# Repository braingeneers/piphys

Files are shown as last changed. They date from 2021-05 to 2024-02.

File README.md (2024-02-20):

# piphys

Update: The latest manuscript about Piphys has been published in IOP Journal of Neural Engineering!

Peer-reviewed journal article: 

[Light-weight electrophysiology hardware and software platform for cloud-based neural recording experiments](https://iopscience.iop.org/article/10.1088/1741-2552/ac310a/pdf)

The original [preprint](https://www.biorxiv.org/content/10.1101/2021.05.18.444685v2) can still be accessed on bioRxiv.

--------
## Overview

Piphys is an inexpensive open source neurophysiological recording platform based on Raspberry Pi. It is easily accessed and controlled via a standard web interface through Internet of Things (IoT) protocols. 

Piphys modules can be used in a fleet to enable long-term observations of neural development, organization, and activity at scale. 

## Design Files

### Hardware
- Raspberry Pi expansion circuit board for and Intan RHD2000 bioamplifier chip.
- Electrode adapter circuit board for Axion CytoView MEA Plate.

Source files, documentation, and files for manufacturing each circuit board are in [`./Hardware`](https://github.com/braingeneers/piphys/tree/main/Hardware).

#### Electrode mapping

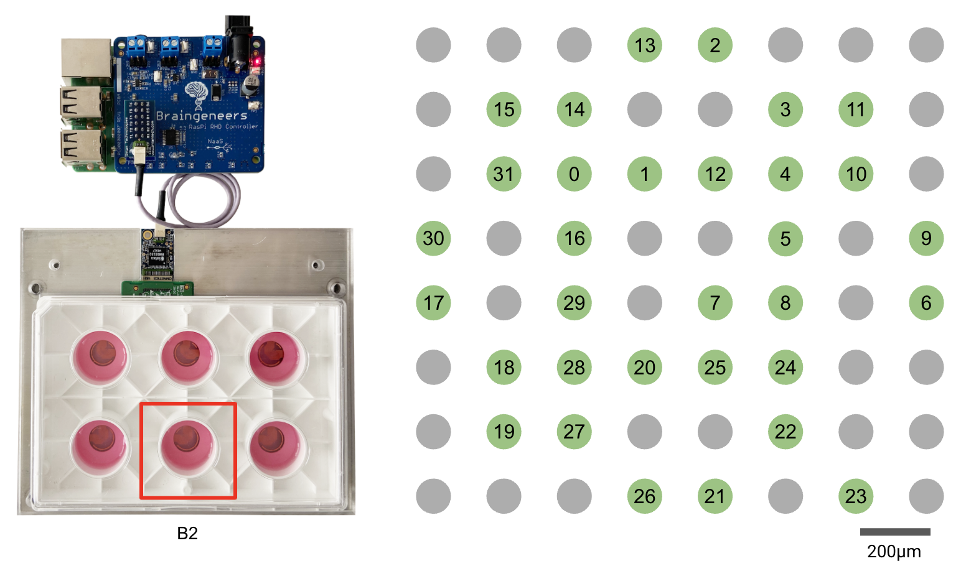
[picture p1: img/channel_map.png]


There are 64 electrodes in a well B2 of the Axion CytoView MEA Plate. The electrode adapter circuit board allows 32 of the 64 electrodes to be recorded by Piphys. The green dots are the recorded channels, labeled with their channel number in the data file sampling sequence.

### Mechanical
CAD files in for the electrode plate holder are in [`./Mechanical/AxionPlateHolder`](https://github.com/braingeneers/piphys/tree/main/Mechanical/AxionPlateHolder).

Assembly Order:
```
AxionPlateHolder_CNC_ClampTop_Aluminum
---------------------------------------
[Axion CytoView MEA Plate]
---------------------------------------
AxionPlateHolder_CNC_ClampBottom_Plastic
AxionPlateHolder_CNC_ClampBottom_Aluminum
```

### Software
Software to enable voltage sampling and user interaction, with accompanying documentation are in [`./Software`](https://github.com/braingeneers/piphys/tree/main/Software).

See [`braingeneerpy`](https://github.com/braingeneers/braingeneerspy) Python package for IoT communication library.

### Test Data
System validation data with sine wave are available at the Piphys [`Google Drive folder`](https://drive.google.com/drive/folders/1S5Uj3old0Q09hUaioH9NGgg6K85ICtAz?usp=sharing).

----
### UC Santa Cruz (UCSC) Noncommercial License

Acceptance

In order to get any license under these terms, you must agree to them as both strict obligations and conditions to all your licenses.

Copyright License

The licensor grants you a copyright license for the repository to do everything you might do with the repository that would otherwise infringe the licensor's copyright in it for any permitted purpose.

Notices

You must ensure that anyone who gets a copy of any part of the repository from you also gets a copy of these terms, as well as the following copyright notice:

This repository is Copyright © 2021. The Regents of the University of California (“Regents”). All Rights Reserved.

Noncommercial Purposes

Any noncommercial purpose is a permitted purpose.

Commercial Purposes

Contact Innovation Transfer, UC Santa Cruz, techno@ucsc.edu , https://officeofresearch.ucsc.edu/iatc/ , for any commercial purpose.

Personal Uses

Personal use for research, experiment, and testing for the benefit of public knowledge, personal study, private entertainment, hobby projects, amateur pursuits, or religious observance, without any anticipated commercial application, is use for a permitted purpose.

Noncommercial Organizations

Use by any charitable organization, educational institution, public research organization, public safety or health organization, environmental protection organization, or government institution is use for a permitted purpose regardless of the source of funding or obligations resulting from the funding.

Fair Use

You may have "fair use" rights for the repository under the law. These terms do not limit them.

No Other Rights

These terms do not allow you to sublicense or transfer any of your licenses to anyone else, or prevent the licensor from granting licenses to anyone else.  These terms do not imply any other licenses.

Patent Defense

If you make any written claim that the repository infringes or contributes to infringement of any patent, all your licenses for the repository granted under these terms end immediately. If your company makes such a claim, all your licenses end immediately for work on behalf of your company.

Violations

The first time you are notified in writing that you have violated any of these terms, or done anything with the repository not covered by your licenses, your licenses can nonetheless continue if you come into full compliance with these terms, and take practical steps to correct past violations, within 32 days of receiving notice.  Otherwise, all your licenses end immediately.

No Liability

As far as the law allows, the repository comes as is, without any warranty or condition, and the licensor will not be liable to you for any damages arising out of these terms or the use or nature of the repository, under any kind of legal claim.

Definitions

The "licensor" is Regents, and the "repository" is the repository the licensor makes available under these terms.

"You" refers to the individual or entity agreeing to these terms.

"Your company" is any legal entity, sole proprietorship, or other kind of organization that you work for, plus all organizations that have control over, are under the control of, or are under common control with that organization.  

"Control" means ownership of substantially all the assets of an entity, or the power to direct its management and policies by vote, contract, or otherwise.  Control can be direct or indirect.

"Your licenses" are all the licenses granted to you for the repository under these terms.

"Use" means anything you do with the repository requiring one of your licenses.

© 2021 Braingeneers

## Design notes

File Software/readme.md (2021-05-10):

# Raspberry Pi - intan RHD Software with IoT interface

## Enviornment Setup:
  Libraries and dependencies are installed to default path /usr/local
- ### bcm2835 
  C library for Broadcom BCM 2835 to access SPI. *[Link](https://www.airspayce.com/mikem/bcm2835/)*    
  
  __Install:__
  ```
  # download the latest version of the library, say bcm2835-1.xx.tar.gz, then:
  tar zxvf bcm2835-1.xx.tar.gz 
  cd bcm2835-1.xx
  ./configure
  make
  sudo make check
  sudo make install     
  ```

- ### redis-plus-plus
  C++ client library for Redis. *[Link](https://github.com/sewenew/redis-plus-plus)*  
  
  __Install:__
  ```
  # first install hiredis
  git clone https://github.com/redis/hiredis.git
  cd hiredis
  make
  make install
  
  # then install redis-plus-plus with cmake
  git clone https://github.com/sewenew/redis-plus-plus.git
  cd redis-plus-plus
  mkdir compile
  cd compile
  cmake -DCMAKE_BUILD_TYPE=Release ..
  make
  make install
  cd ..
  ```
  
- ### JsonCpp
  C++ library to manipulate Json files. *[Link](https://github.com/open-source-parsers/jsoncpp)*
  
  __Install:__
  ```
  sudo apt-get install libjsoncpp-dev
  ```
  - __Note:__ Using the vcpkg dependency manager as said in the instruction on JsonCpp's github page may stuck the pi. The header file using *apt-get install* should be included as <jsoncpp/json/json.h>.

- ### AWS IOT Cpp
  Library and examples for using AWS IOT device. *[Link](https://github.com/aws/aws-iot-device-sdk-cpp-v2)*
  
  __Install:__
  ```
  mkdir sdk-cpp-workspace
  cd sdk-cpp-workspace
  git clone --recursive https://github.com/aws/aws-iot-device-sdk-cpp-v2.git
  mkdir aws-iot-device-sdk-cpp-v2-build
  cd aws-iot-device-sdk-cpp-v2-build
  cmake -DCMAKE_INSTALL_PREFIX="/usr/local"  -DBUILD_DEPS=ON ../aws-iot-device-sdk-cpp-v2
  cmake --build . --target install   
  ```

- ### AWS S3/prp
  Long term data file storage.
  
  __Install:__
  ```
  pip install awscli-plugin-endpoint
  ```
  __Credentials:__ 
  Find or ask Key and Secret on *prp-dash-helpdesk* channel on Slack then put them at ~/.aws/credentials
  
  __Check the endpoint:__
  ```
  aws --profile prp --endpoint https://s3.nautilus.optiputer.net s3 ls s3://braingeneers/archive/ephysDebugging/
  ```

 ## Application Compile and Run   

  __Compile:__
  ```
  mkdir build
  cd build
  cmake -DCMAKE_PREFIX_PATH=/usr/local  -DCMAKE_BUILD_TYPE=Release ..
  cmake --build . --config Release
  cd ..
  ```

  __Run:__
  ```
  sudo ./rhd_datastream
  ```
<!-- Json rules for AWS IOT: -->

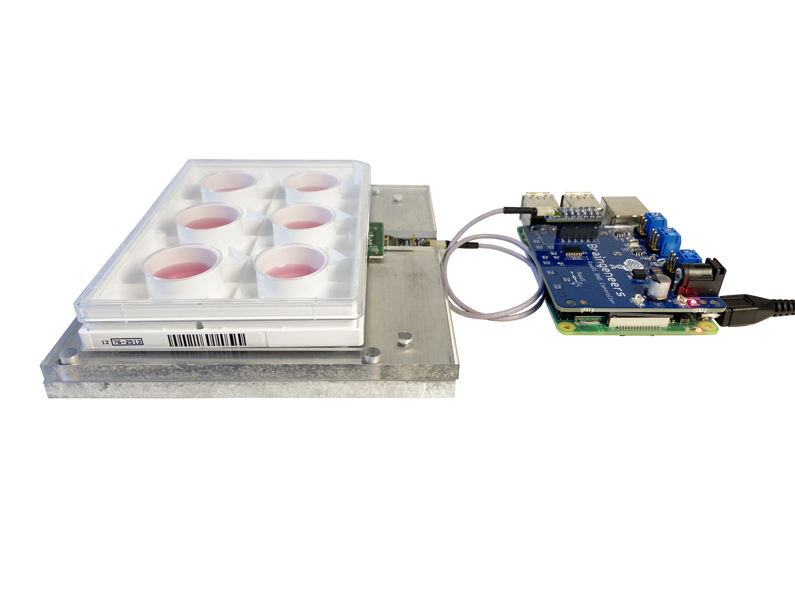
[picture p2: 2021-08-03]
img/side.png

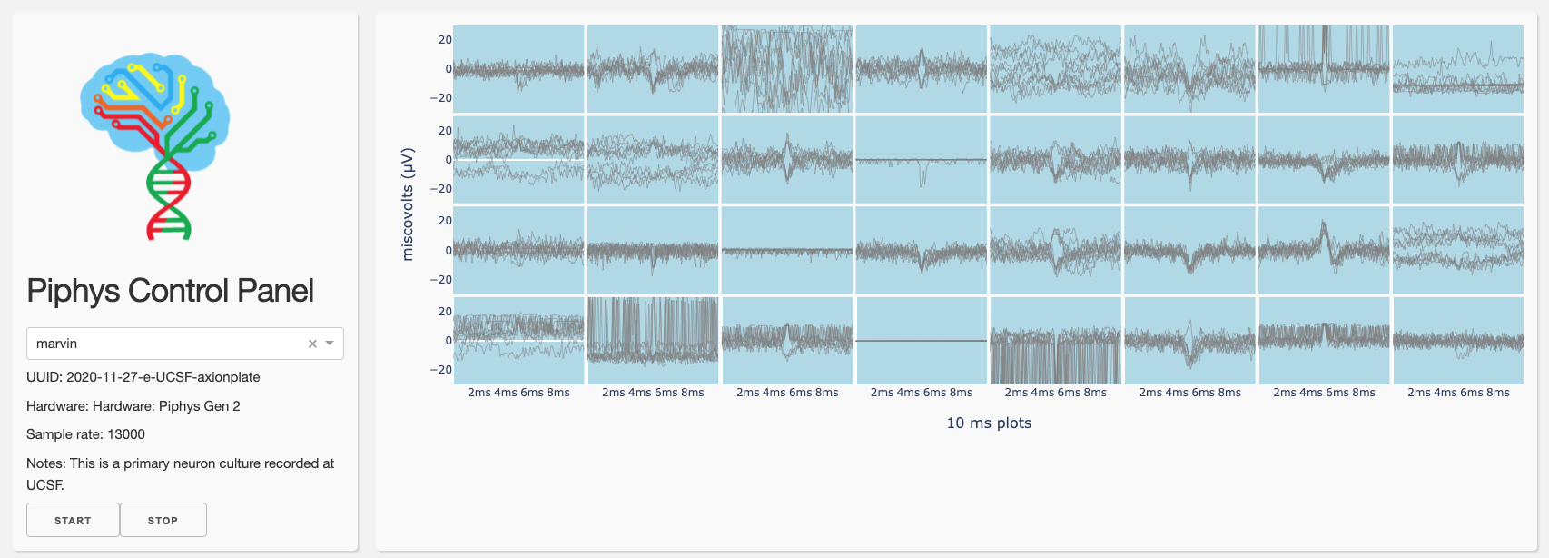
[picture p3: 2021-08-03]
img/dashboard.png

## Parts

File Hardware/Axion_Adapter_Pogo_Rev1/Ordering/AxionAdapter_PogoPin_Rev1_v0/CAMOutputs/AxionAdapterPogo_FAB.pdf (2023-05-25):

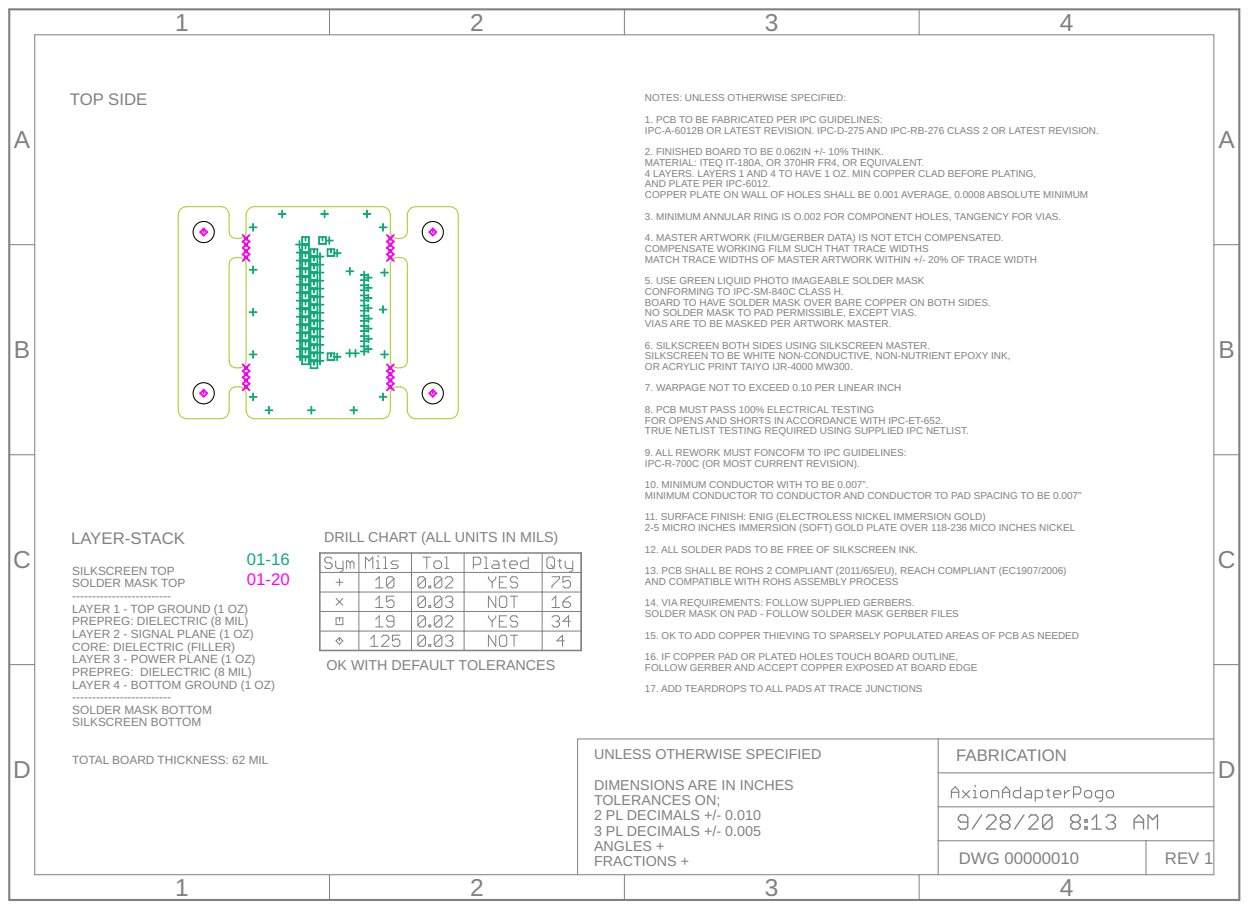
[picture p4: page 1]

NOTES: UNLESS OTHERWISE SPECIFIED: 1. PCB TO BE FABRICATED PER IPC GUIDELINES:

IPC-A-6012B OR LATEST REVISION. IPC-D-275 AND IPC-RB-276 CLASS 2 OR LATEST REVISION. 2. FINISHED BOARD TO BE 0.062IN +/- 10% THINK. MATERIAL: ITEQ IT-180A, OR 370HR FR4, OR EQUIVALENT. 4 LAYERS. LAYERS 1 AND 4 TO HAVE 1 OZ. MIN COPPER CLAD BEFORE PLATING, AND PLATE PER IPC-6012. COPPER PLATE ON WALL OF HOLES SHALL BE 0.001 AVERAGE, 0.0008 ABSOLUTE MINIMUM

3. MINIMUM ANNULAR RING IS O.002 FOR COMPONENT HOLES, TANGENCY FOR VIAS. 4. MASTER ARTWORK (FILM/GERBER DATA) IS NOT ETCH COMPENSATED. COMPENSATE WORKING FILM SUCH THAT TRACE WIDTHS MATCH TRACE WIDTHS OF MASTER ARTWORK WITHIN +/- 20% OF TRACE WIDTH

5. USE GREEN LIQUID PHOTO IMAGEABLE SOLDER MASK CONFORMING TO IPC-SM-840C CLASS H. BOARD TO HAVE SOLDER MASK OVER BARE COPPER ON BOTH SIDES. NO SOLDER MASK TO PAD PERMISSIBLE, EXCEPT VIAS. VIAS ARE TO BE MASKED PER ARTWORK MASTER. 6. SILKSCREEN BOTH SIDES USING SILKSCREEN MASTER. SILKSCREEN TO BE WHITE NON-CONDUCTIVE, NON-NUTRIENT EPOXY INK, OR ACRYLIC PRINT TAIYO IJR-4000 MW300. 7. WARPAGE NOT TO EXCEED 0.10 PER LINEAR INCH

8. PCB MUST PASS 100% ELECTRICAL TESTING
FOR OPENS AND SHORTS IN ACCORDANCE WITH IPC-ET-652. TRUE NETLIST TESTING REQUIRED USING SUPPLIED IPC NETLIST. 9. ALL REWORK MUST FONCOFM TO IPC GUIDELINES:

IPC-R-700C (OR MOST CURRENT REVISION). 10. MINIMUM CONDUCTOR WITH TO BE 0.007”. MINIMUM CONDUCTOR TO CONDUCTOR AND CONDUCTOR TO PAD SPACING TO BE 0.007” 11. SURFACE FINISH: ENIG (ELECTROLESS NICKEL IMMERSION GOLD) 2-5 MICRO INCHES IMMERSION (SOFT) GOLD PLATE OVER 118-236 MICO INCHES NICKEL

DRILL CHART (ALL UNITS IN MILS)

12. ALL SOLDER PADS TO BE FREE OF SILKSCREEN INK. 13. PCB SHALL BE ROHS 2 COMPLIANT (2011/65/EU), REACH COMPLIANT (EC1907/2006) AND COMPATIBLE WITH ROHS ASSEMBLY PROCESS

SILKSCREEN TOP
SOLDER MASK TOP
------------------------- LAYER 1 - TOP GROUND (1 OZ) PREPREG: DIELECTRIC (8 MIL) LAYER 2 - SIGNAL PLANE (1 OZ) CORE: DIELECTRIC (FILLER) LAYER 3 - POWER PLANE (1 OZ) PREPREG: DIELECTRIC (8 MIL) LAYER 4 - BOTTOM GROUND (1 OZ)

14. VIA REQUIREMENTS: FOLLOW SUPPLIED GERBERS. SOLDER MASK ON PAD - FOLLOW SOLDER MASK GERBER FILES

15. OK TO ADD COPPER THIEVING TO SPARSELY POPULATED AREAS OF PCB AS NEEDED

OK WITH DEFAULT TOLERANCES

16. IF COPPER PAD OR PLATED HOLES TOUCH BOARD OUTLINE, FOLLOW GERBER AND ACCEPT COPPER EXPOSED AT BOARD EDGE

17. ADD TEARDROPS TO ALL PADS AT TRACE JUNCTIONS

TOTAL BOARD THICKNESS: 62 MIL

DIMENSIONS ARE IN INCHES
TOLERANCES ON; 2 PL DECIMALS +/- 0.010

3 PL DECIMALS +/- 0.005 ANGLES + FRACTIONS +

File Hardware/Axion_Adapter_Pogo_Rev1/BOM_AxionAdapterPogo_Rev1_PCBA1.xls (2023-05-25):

Bill of Materials |  |  | Axion Adapter Pogo Rev1 PCBA1 |  |  | Braingeneers
Component Description | QTY | Ref. Des | Value | Package | Digi-Key part number | Manufacturer | Manufacturer Part # (MPN) | Notes | Side | SMD/thru-hole
CONTACT SPRING LOADED T/H GOLD | 34 | P1, P2, P3, P4, P5, P6, P7, P8, P9, P10, P11, P12, P13, P14, P15, P16, P17, P18, P19, P20, P21, P22, P23, P24, P25, P26, P27, P28, P29, P30, P31, P32, P33, P34 | 0985-0-15-20-71-14-11-0 | -- | ED1122-ND | Mill-Max Manufacturing Corp. | 0985-0-15-20-71-14-11-0 | pogo pins sticking upward from board top side | top | thru-hole
Omnetics A79024 36-pin connector | 1 | S1 | OMNETICS_A79024 | NPD-36-AA-GS | N/A | Omnetics Connector Corporation | A79024-001 | Back-ordered online, parts will be delivered by mail from our stock | top | SMD

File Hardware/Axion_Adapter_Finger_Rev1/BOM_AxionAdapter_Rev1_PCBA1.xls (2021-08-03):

Bill of Materials |  |  | Axion Adapter Rev1 PCBA1 |  |  | Braingeneers
Component Description | QTY | Ref. Des | Value | Package | Digi-Key part number | Manufacturer | Manufacturer Part # (MPN) | Notes | Side | SMD/thru-hole
SPRING FINGER 1.45H | 34 | P1, P2, P3, P4, P5, P6, P7, P8, P9, P10, P11, P12, P13, P14, P15, P16, P17, P18, P19, P20, P21, P22, P23, P24, P25, P26, P27, P28, P29, P30, P31, P32, P33, P34 | 2336713-2_TE | -- | A142210CT-ND | TE Connectivity AMP Connectors | 2336713-2 | Contact pin side faces the double line on silkscreen | bottom | SMD
Omnetics A79024 36-pin connector | 1 | S1 | OMNETICS_A79024 | NPD-36-AA-GS | N/A | Omnetics Connector Corporation | A79024-001 | Back-ordered online, we will send this part by mail from our stock | top | SMD

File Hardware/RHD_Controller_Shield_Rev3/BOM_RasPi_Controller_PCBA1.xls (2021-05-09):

Bill of Materials |  |  | RasPi Controller RHD Rev1 PCBA1 |  |  | Braingeneers
Component Description | QTY | Ref. Des | Value | Package | Digi-Key part number | Manufacturer | Manufacturer Part # (MPN) | Notes | Side | SMD/thru-hole
Red 633nm LED Indication - Discrete 2V 0603 (1608 Metric) | 1 | PWR | -- | CHIPLED_0603 | 475-2512-1-ND | OSRAM Opto Semiconductors Inc. | LS Q976-NR-1 | N/A | top | SMD
1µF ±10% 25V Ceramic Capacitor X5R 0603 (1608 Metric) | 2 | C1, C2 | 1.0uF | 0603 | 1276-1102-1-ND | Samsung Electro-Mechanics | CL10A105KA8NNNC | N/A | top | SMD
22µF ±20% 16V Ceramic Capacitor X5R 0603 (1608 Metric) | 2 | C3, C4, C5, C6 | 22uF | 0603 | 1276-7076-1-ND | Samsung Electro-Mechanics | CL10A226MO7JZNC | N/A | top | SMD
10000pF ±10% 16V Ceramic Capacitor X7R 0201 (0603 Metric) | 4 | C7, C8, C9, C10 | 10 nF (10000 pF) | 0201 | 311-1404-1-ND | Yageo | CC0201KRX7R7BB103 | N/A | top | SMD
0.1µF ±10% 16V Ceramic Capacitor X5R 0201 (0603 Metric) | 5 | C11, C12, C13, C14, C15 | 100 nF (0.1 uF) | 0201 | 490-9985-1-ND | Murata Electronics | GRM033R61C104KE84D | N/A | top | SMD
15pF ±5% 50V Ceramic Capacitor C0G, NP0 0201 (0603 Metric) | 1 | C16 | 15pF | 0201 | 311-1396-1-ND | Yageo | CC0201JRNPO9BN150 | N/A | top | SMD
100µF 25V Aluminum Electrolytic Capacitors Radial, Can - SMD 1000 Hrs @ 105°C | 1 | C17 | 100uF | EEE-HAE101XAP | PCE4706CT-ND | Panasonic Electronic Components | EEE-HAE101XAP | N/A | top | SMD
22.1 Ohms ±1% 0.063W, 1/16W Chip Resistor 0402 (1005 Metric) Moisture Resistant Thick Film | 4 | R1, R2, R3, R4 | 22.1 | 0402 | YAG1256CT-ND | Yageo | RC0402FR-0722R1P | N/A | top | SMD
56 Ohms ±5% 0.063W, 1/16W Chip Resistor 0402 (1005 Metric) Moisture Resistant Thick Film | 1 | R5 | 56.0K | 0402 | 311-56JRCT-ND | Yageo | RC0402JR-0756RL | N/A | top | SMD
30.1 Ohms ±1% 0.063W, 1/16W Chip Resistor 0402 (1005 Metric) Moisture Resistant Thick Film | 1 | R6 | 30.1K | 0402 | YAG3111CT-ND | Yageo | RC0402FR-0730R1L | N/A | top | SMD
0 Ohms Jumper 0.063W, 1/16W Chip Resistor 0402 (1005 Metric) Moisture Resistant Thick Film | 5 | R7, R8, R9, R10, R17 | 0 | 0402 | 311-0.0JRCT-ND | Yageo | RC0402JR-070RL | Leave others unstuffed (R11, R12, R13, R14, R15, R16, R18, R19) | top | SMD
1 kOhms ±1% 0.063W, 1/16W Chip Resistor 0402 (1005 Metric) Moisture Resistant Thick Film | 1 | R20 | 1K | 0402 | 311-1.00KLRCT-ND | Yageo | RC0402FR-071KL | N/A | top | SMD
120 Ohms @ 100MHz 1 Signal Line Ferrite Bead 0402 (1005 Metric) 300mA 700mOhm | 3 | FB1, FB2, FB3 | BLM15HB121SN1 | 0402 | 490-4000-2-ND | Murata Electronics | BLM15HB121SN1D | N/A | top | SMD
Power Barrel Connector Jack 2.00mm ID (0.079"), 5.50mm OD (0.217") Through Hole, Right Angle | 1 | J1 | DC_POWER_JACK-PJ-102AH | PJ-102AH | CP-102AH-ND | CUI Devices | PJ-102AH | N/A | top | Thru-hole
Polymeric PTC Resettable Fuse 16V 2.5A Ih Surface Mount 1812 (4532 Metric), Concave | 1 | F1 | MF-MSMF250/X | MF-MSMF250/16X-2 | MF-MSMF250/16X-2CT-ND | Bourns Inc. | MF-MSMF250/16X-2 | N/A | top | SMD
9.2V Clamp 65.3A Ipp Tvs Diode Surface Mount DO-214AA (SMBJ) | 1 | CR1 | SMBJ5.0A | DIODE_DO214AA | SMBJ5.0ALFTR-ND | Littelfuse Inc. | SMBJ5.0A | N/A | top | SMD
4/1 Transceiver Half LVDS 20-TSSOP | 1 | U1 | SN65LVDT41 | 20-TSSOP | 296-12738-5-ND | Texas Instruments | SN65LVDT41PW | N/A | top | SMD
12 Position Receptacle, Pass Through Connector Surface Mount | 1 | S1 | RHD2000-CABLE-DAQ-SIDEINTAN_SMT_SPI_CABLE_ADAPTER | -- | SAM1146-06-ND | Samtec Inc. | SSM-106-L-DV | N/A | top | SMD
2 Position Wire to Board Terminal Block Horizontal with Board 0.138" (3.50mm) Through Hole | 3 | S2, S3, S4 | OSTTE020161 | -- | ED2635-ND | On Shore Technology Inc. | OSTTE020161 | N/A | top | Thru-hole
Linear Voltage Regulator IC 1 Output 200mA SOT-23-6 | 1 | U2 | TPS79301 | SOT-23-6 | 296-12154-1-ND | Texas Instruments | TPS79301DBVR | N/A | top | SMD
Linear Voltage Regulator IC 1 Output 200mA SOT-23-5 | 1 | U4 | TPS79333 | TSOT-23-5 | 296-12961-1-ND | Texas Instruments | TPS79333DBVR | N/A | top | SMD
PC Test Point, Compact Phosphor Bronze, Silver Plating Surface Mount Mounting Type | 6 | TP1, TP2, TP3, TP4, TP5, TP6 | PC TEST POINT COMPACT | -- | 36-5016CT-ND | Keystone Electronics | 5016 | N/A | top | SMD
40 Position Receptacle Connector Surface Mount | 1 | CN1 | HLE-120-02-L-DV | SAMTEC-HLE-120-02-X-DV | SAM15669-ND | Samtec Inc. | HLE-120-02-L-DV | N/A | bottom | SMD
Connector Header Through Hole 3 position 0.100" (2.54mm) | 3 | JP1, JP2, JP3 | CONN HEADER VERT 3POS 2.54MM | 1X03 | SAM1029-03-ND | Samtec Inc. | TSW-103-07-G-S | N/A | top | Thru-hole
 |  |  |  |  |  |  |  |  |  |  |  | Raspi Controller Turnkey (Fab + Assembly + Components) Price
 |  |  |  |  |  |  |  |  |  |  |  | $302.88 | ea. by Sierra Circuits (5 day fab + 5 day assembly, from quote on 10 boards)
For internal reference, not included in assembly:
2 (1 x 2) Position Shunt Connector Open Top 0.100" (2.54mm) Gold | 3 | N/A | -- | -- | S9342-ND | Sullins Connector Solutions | SPC02SXCN-RC | Jumpers for JP1, JP2, JP3 | top | N/A
RHD SPI cable adapter board | 1 | N/A | -- | -- | N/A | Intan Technologies LLC | C3430 | Mates with S2 | top | N/A |  | $98
RHD 3-ft (0.9 m) standard SPI cable | 1 | N/A | -- | -- | N/A | Intan Technologies LLC | C3203 |  | N/A | N/A |  | $215
RHD 32-channel headstage (https://intantech.com/RHD_headstages.html?tabSelect=RHD32ch) | 1 | N/A | -- | -- | N/A | Intan Technologies LLC | C3314 |  | N/A | N/A |  | $895
Raspberry Pi B+ | 1 | N/A | -- | -- | N/A | Adafruit Industries | 3775 | Single board computer | N/A | N/A |  | $35
 |  |  |  |  |  |  |  |  |  |  | TOTAL Price: | $1545.88

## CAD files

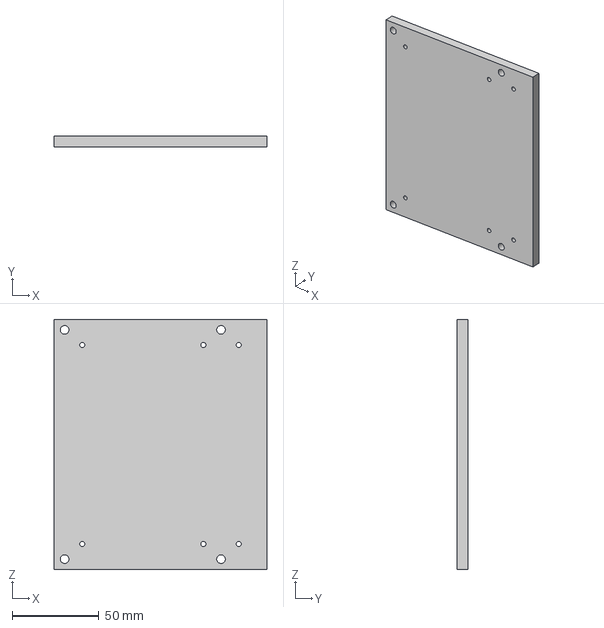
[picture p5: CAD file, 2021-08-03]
Mechanical/AxionPlateHolder/AxionPlateHolder_CNC_Simple_ClampBottom_Aluminum.step
122.8 x 6.45 x 144.5 mm

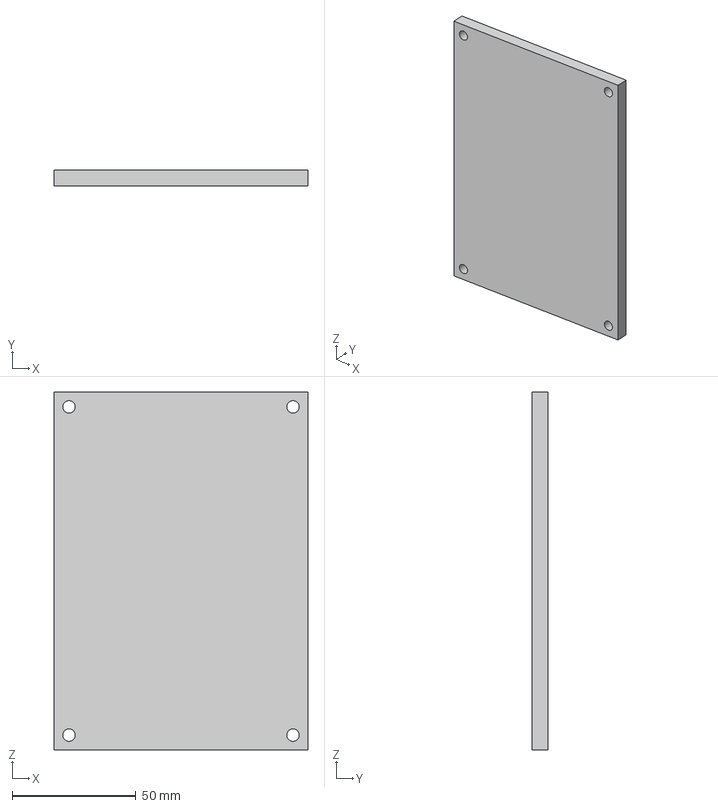
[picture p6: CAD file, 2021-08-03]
Mechanical/AxionPlateHolder/AxionPlateHolder_CNC_ClampTop_Aluminum.step
102.4 x 6.45 x 144.5 mm

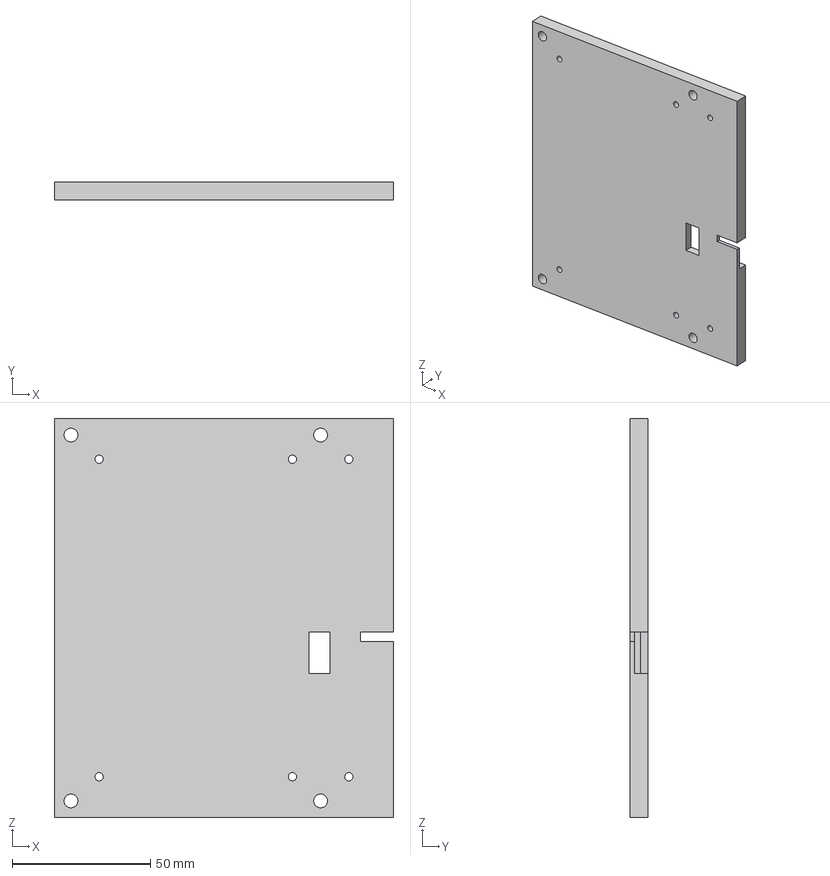
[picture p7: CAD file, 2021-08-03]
Mechanical/AxionPlateHolder/AxionPlateHolder_CNC_ClampBottom_Plastic.step
122.8 x 6.45 x 144.5 mm

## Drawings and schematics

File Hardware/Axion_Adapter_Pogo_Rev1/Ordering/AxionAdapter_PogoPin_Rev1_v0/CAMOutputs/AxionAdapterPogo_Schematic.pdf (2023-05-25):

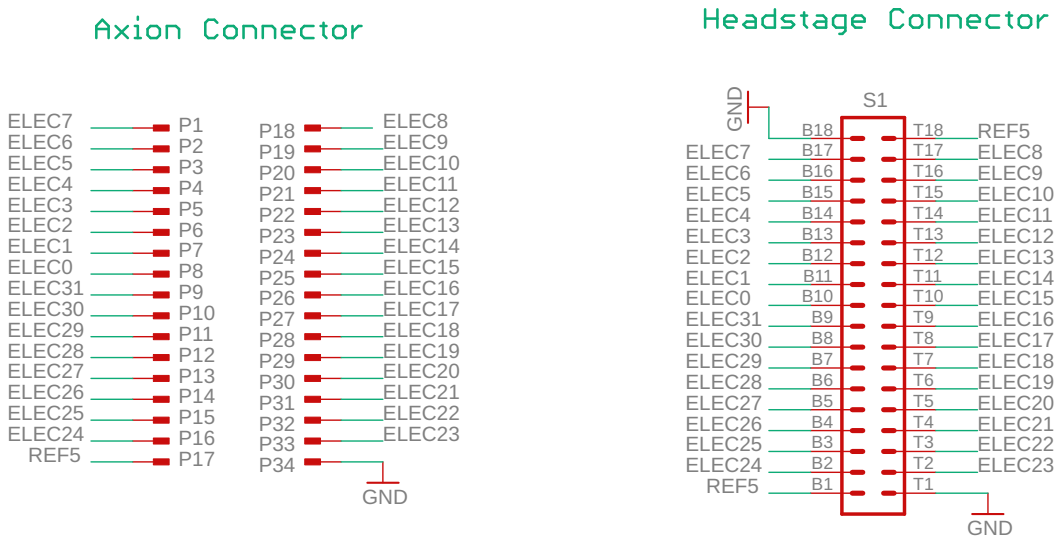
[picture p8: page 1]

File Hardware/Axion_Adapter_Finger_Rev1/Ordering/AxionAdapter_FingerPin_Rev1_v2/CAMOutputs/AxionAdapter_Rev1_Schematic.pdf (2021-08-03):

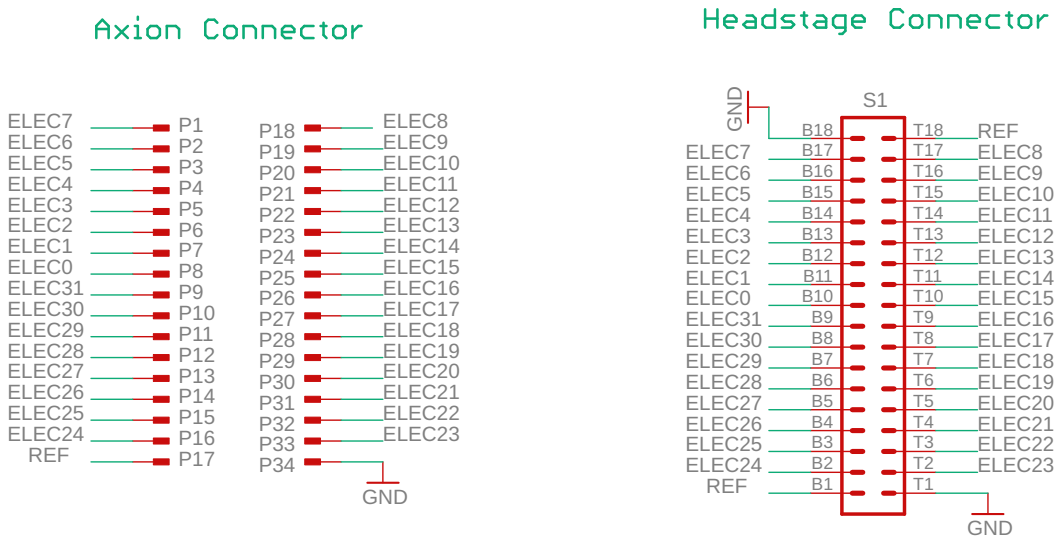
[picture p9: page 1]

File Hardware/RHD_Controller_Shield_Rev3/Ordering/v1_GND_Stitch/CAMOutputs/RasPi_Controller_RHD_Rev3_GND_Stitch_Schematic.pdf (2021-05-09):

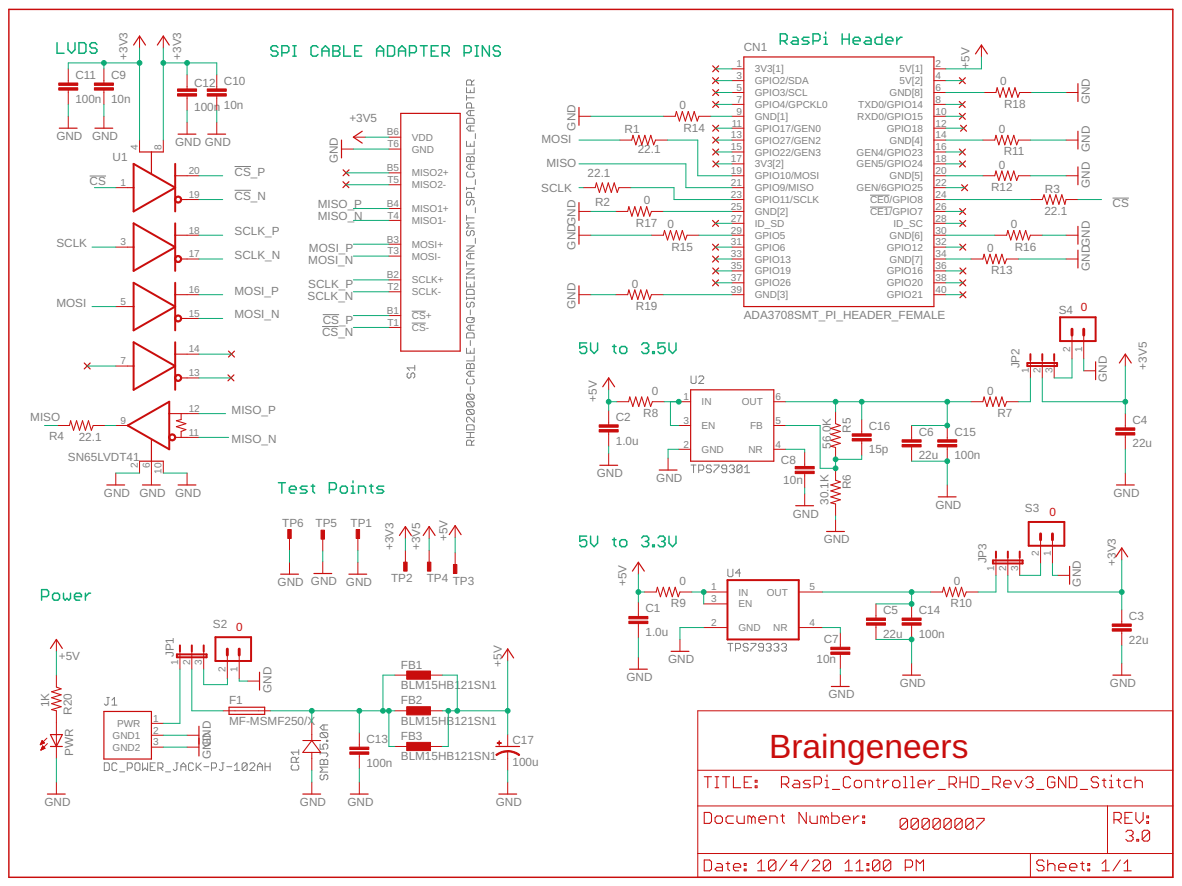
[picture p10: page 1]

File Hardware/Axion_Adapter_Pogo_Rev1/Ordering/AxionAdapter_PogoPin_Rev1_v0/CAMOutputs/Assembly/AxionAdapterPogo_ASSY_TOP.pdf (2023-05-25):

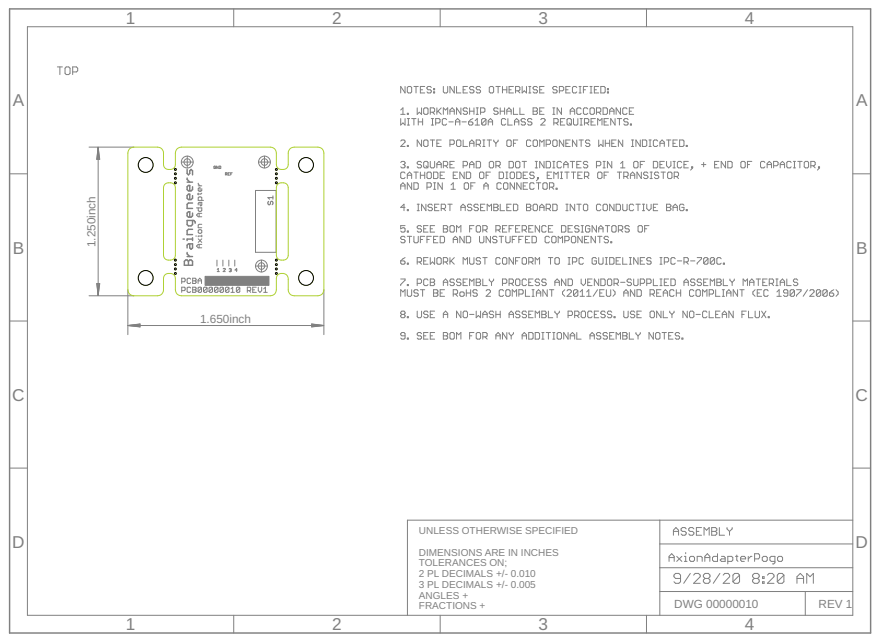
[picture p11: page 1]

UNLESS OTHERWISE SPECIFIED DIMENSIONS ARE IN INCHES TOLERANCES ON; 2 PL DECIMALS +/- 0.010 3 PL DECIMALS +/- 0.005 ANGLES + FRACTIONS +

DWG 00000010 | REV 1

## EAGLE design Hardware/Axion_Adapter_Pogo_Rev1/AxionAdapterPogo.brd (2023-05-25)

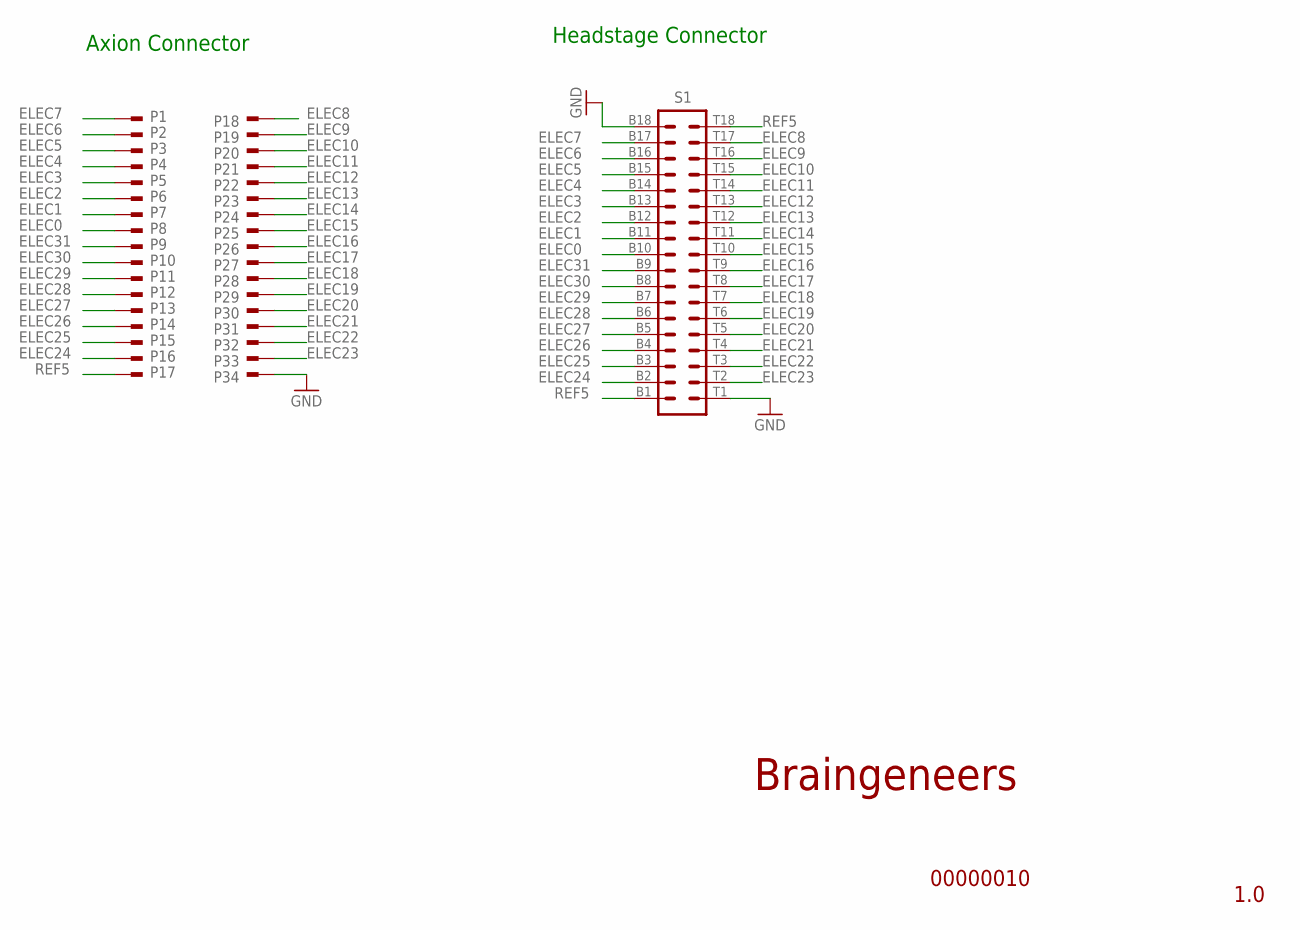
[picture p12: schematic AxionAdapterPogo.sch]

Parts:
P1, P2, P3, P4, P5, P6, P7, P8, P9, P10, P11, P12, P13, P14, P15, P16, P17, P18, P19, P20, P21, P22, P23, P24, P25, P26, P27, P28, P29, P30, P31, P32, P33, P34: MILL-MAX_POGO_0985-0-15-20-71-14-11-0
S1: OMNETICS_A79024

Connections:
ELEC0: P8.P$1, S1.B10
ELEC1: P7.P$1, S1.B11
ELEC2: P6.P$1, S1.B12
ELEC3: P5.P$1, S1.B13
ELEC4: P4.P$1, S1.B14
ELEC5: P3.P$1, S1.B15
ELEC6: P2.P$1, S1.B16
ELEC7: P1.P$1, S1.B17
ELEC8: P18.P$1, S1.T17
ELEC9: P19.P$1, S1.T16
ELEC10: P20.P$1, S1.T15
ELEC11: P21.P$1, S1.T14
ELEC12: P22.P$1, S1.T13
ELEC13: P23.P$1, S1.T12
ELEC14: P24.P$1, S1.T11
ELEC15: P25.P$1, S1.T10
ELEC16: P26.P$1, S1.T9
ELEC17: P27.P$1, S1.T8
ELEC18: P28.P$1, S1.T7
ELEC19: P29.P$1, S1.T6
ELEC20: P30.P$1, S1.T5
ELEC21: P31.P$1, S1.T4
ELEC22: P32.P$1, S1.T3
ELEC23: P33.P$1, S1.T2
ELEC24: P16.P$1, S1.B2
ELEC25: P15.P$1, S1.B3
ELEC26: P14.P$1, S1.B4
ELEC27: P13.P$1, S1.B5
ELEC28: P12.P$1, S1.B6
ELEC29: P11.P$1, S1.B7
ELEC30: P10.P$1, S1.B8
ELEC31: P9.P$1, S1.B9
GND: P34.P$1, S1.B18, S1.T1
REF5: P17.P$1, S1.B1, S1.T18

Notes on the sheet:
1.0
00000010
Braingeneers
Headstage Connector
Axion Connector

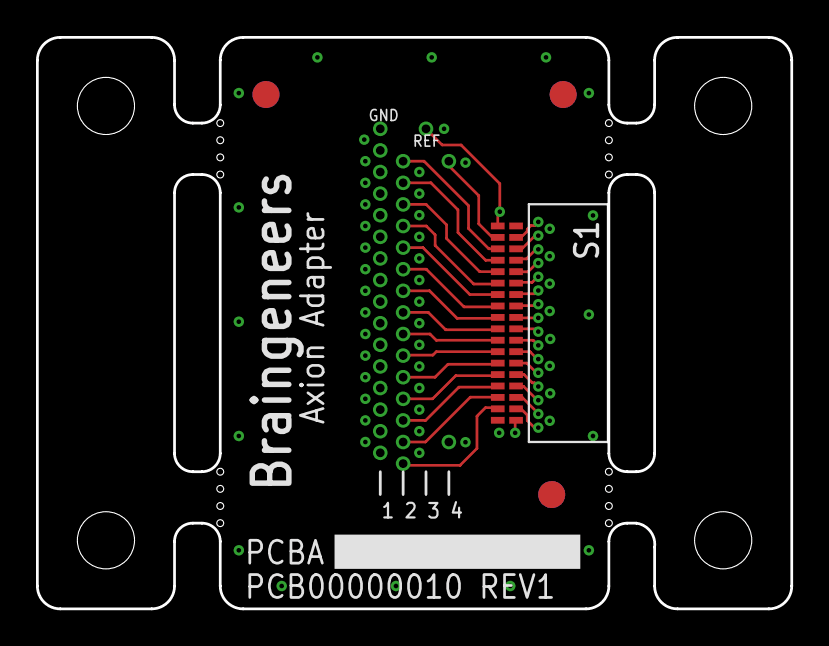
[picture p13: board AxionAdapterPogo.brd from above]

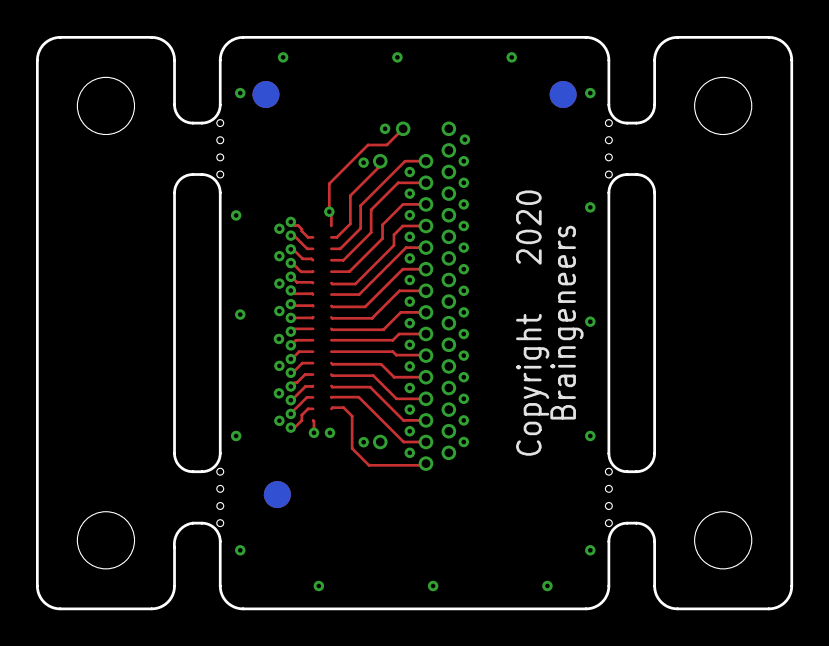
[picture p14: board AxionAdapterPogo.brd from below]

Board: 4 copper layers, 41.9 x 31.8 mm, 48 parts (38 on the bottom side), 34 nets.

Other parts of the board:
DRILEGEND: DRILEGEND
U$1, U$2, U$35, U$49, U$50, U$73: FIDUCIAL_G15
U$7: NASS_LOGO_LG
U$31: ROHS_LG
U$52: A5L-LOC
U$70: NO_TRASH_LG
U$72: STATIC_LG
U$84: COMPYRIGHT_MED

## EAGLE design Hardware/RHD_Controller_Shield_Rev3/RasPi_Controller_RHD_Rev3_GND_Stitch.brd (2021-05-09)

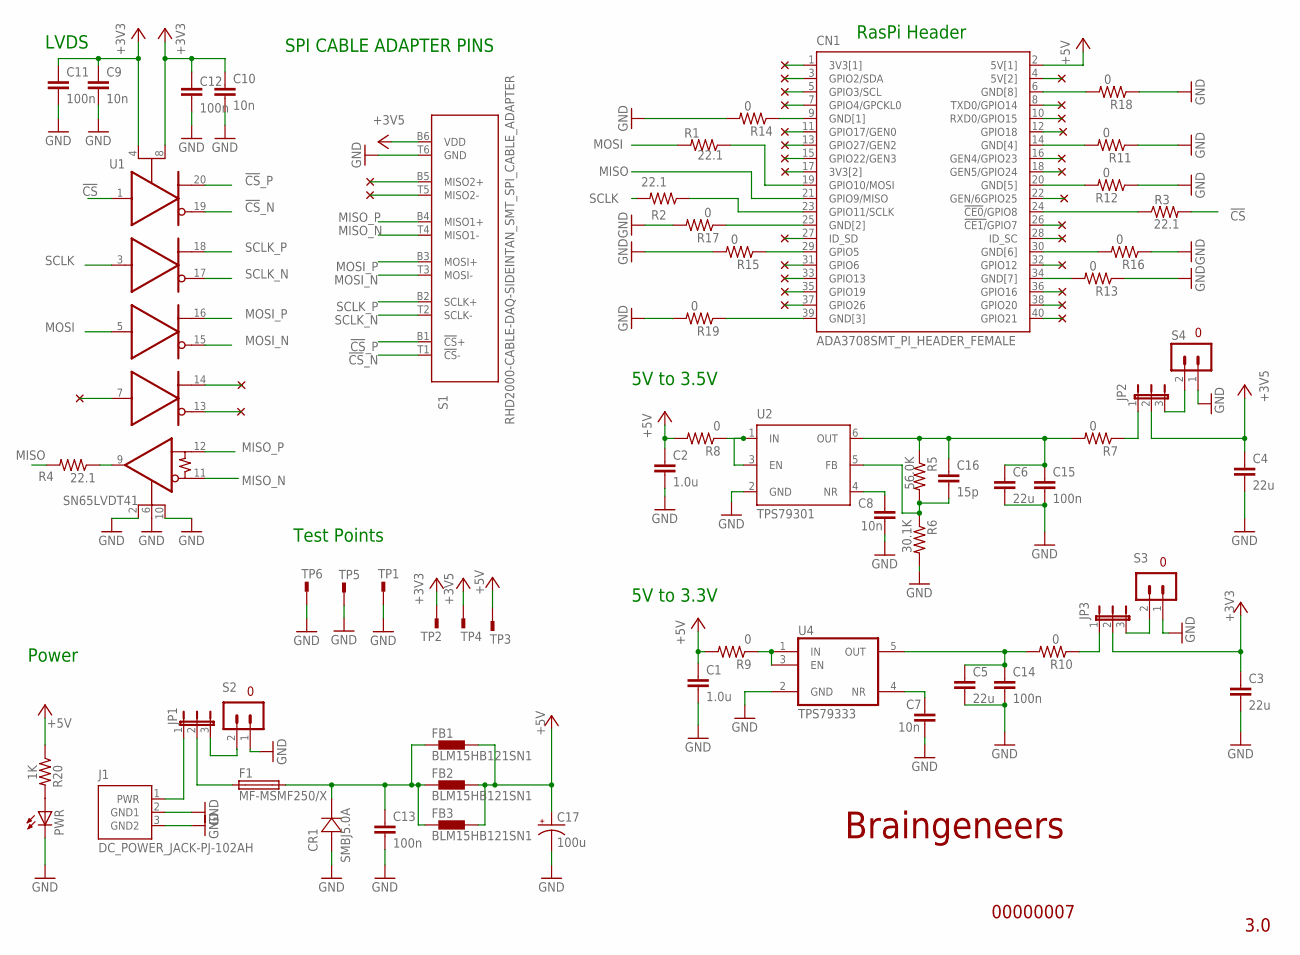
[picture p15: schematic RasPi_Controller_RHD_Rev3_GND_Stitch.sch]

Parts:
C1, C2: 1.0u; 0603
C3, C4, C5, C6: 22u; 0603
C7, C8, C9, C10: 10n; 0201
C11, C12, C13, C14, C15: 100n; 0201
C16: 15p; 0201
C17: 100u; EEE-HAE101XAP
CN1: ADA3708SMT_PI_HEADER_FEMALE; SAMTEC-HLE-120-02-X-DV
CR1: SMBJ5.0A; DIODE_DO214AA
F1: MF-MSMF250/X; MF-MSMF250/16X-2
FB1, FB2, FB3: BLM15HB121SN1; 0402
J1: DC_POWER_JACK-PJ-102AH; PJ-102AH
JP1, JP2, JP3: JP2E; JP2
PWR: LEDCHIPLED_0603; CHIPLED_0603
R1, R2, R3, R4: 22.1; 0402
R5: 56.0K; 0402
R6: 30.1K; 0402
R7, R8, R9, R10, R11, R12, R13, R14, R15, R16, R17, R18, R19: 0; 0402
R20: 1K; 0402
S1: RHD2000-CABLE-DAQ-SIDEINTAN_SMT_SPI_CABLE_ADAPTER; INTAN_SMT_RHD_SPI_CABLE_ADAPTER
S2: TERMINAL_BLOCK_2-3.5MM-5V; TERMINAL_BLOCK_3.5MM_2_5V
S3: TERMINAL_BLOCK_2-3.5MM-3.3V; TERMINAL_BLOCK_3.5MM_2_3.3V
S4: TERMINAL_BLOCK_2-3.5MM-3.5V; TERMINAL_BLOCK_3.5MM_2_3.5V
TP1, TP2, TP3, TP4, TP5, TP6: 5016
U1: SN65LVDT41; TSSOP-20
U2: TPS79301; SOT-23-6
U4: TPS79333; TSOT-23-5

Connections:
!CS!: R3.2, U1.1 (1D)
!CS!_N: S1.T1 (!CS!-), U1.19 (1Z)
!CS!_P: S1.B1 (!CS!+), U1.20 (1Y)
+3V3: C3.1, C9.1, C10.1, C11.1, C12.1, JP3.2, TP2.P$1, U1.4 (VCC1), U1.8 (VCC2)
+3V3_REG: C5.1, C14.1, R10.2, U4.5 (OUT)
+3V5: C4.1, JP2.2, S1.B6 (VDD), TP4.P$1
+5V: C1.1, C2.1, C17.1 (+), CN1.2 (5V[1]), FB1.2, FB2.2, FB3.2, R8.2, R9.2, R20.1, TP3.P$1
+5V_JACK: J1.1 (PWR), JP1.1
GND: C1.2, C2.2, C3.2, C4.2, C5.2, C6.2, C7.2, C8.2, C9.2, C10.2, C11.2, C12.2, C13.2, C14.2, C15.2, C17.2 (-), CR1.2, J1.2 (GND1), J1.3 (GND2), PWR.C, R6.2, R11.1, R12.1, R13.1, R14.2, R15.2, R16.1, R17.2, R18.1, R19.2, S1.T6 (GND), S2.1 (0), S3.1 (0), S4.1 (0), TP1.P$1, TP5.P$1, TP6.P$1, U1.2 (GND1), U1.6 (GND2), U1.10 (GND3), U2.2 (GND), U4.2 (GND)
MISO: CN1.21 (GPIO9/MISO), R4.2
MISO_N: S1.T4 (MISO1-), U1.11 (5B)
MISO_P: S1.B4 (MISO1+), U1.12 (5A)
MOSI: R1.2, U1.5 (3D)
MOSI_N: S1.T3 (MOSI-), U1.15 (3Z)
MOSI_P: S1.B3 (MOSI+), U1.16 (3Y)
unnamed: C13.1, CR1.1, F1.P$2 (2), FB1.1, FB2.1, FB3.1
unnamed: CN1.6 (GND[8]), R18.2
unnamed: CN1.30 (GND[6]), R16.2
unnamed: C8.1, U2.4 (NR)
unnamed: PWR.A, R20.2
unnamed: CN1.25 (GND[2]), R17.1
unnamed: CN1.29 (GPIO5), R15.1
unnamed: CN1.9 (GND[1]), R14.1
unnamed: CN1.14 (GND[4]), R11.2
unnamed: CN1.20 (GND[5]), R12.2
unnamed: CN1.34 (GND[7]), R13.2
unnamed: JP1.3, S2.2 (1)
unnamed: C16.2, R5.2, R6.1, U2.5 (FB)
unnamed: C7.1, U4.4 (NR)
unnamed: R9.1, U4.1 (IN), U4.3 (EN)
unnamed: R8.1, U2.1 (IN), U2.3 (EN)
unnamed: F1.P$1 (1), JP1.2
unnamed: JP3.3, S3.2 (1)
unnamed: JP2.3, S4.2 (1)
unnamed: JP2.1, R7.1
unnamed: JP3.1, R10.1
unnamed: CN1.23 (GPIO11/SCLK), R2.1
unnamed: CN1.24 (!CE0!/GPIO8), R3.1
unnamed: R4.1, U1.9 (5R)
unnamed: CN1.39 (GND[3]), R19.1
unnamed: CN1.19 (GPIO10/MOSI), R1.1
SCLK: R2.2, U1.3 (2D)
SCLK_N: S1.T2 (SCLK-), U1.17 (2Z)
SCLK_P: S1.B2 (SCLK+), U1.18 (2Y)
U2_OUT: C6.1, C15.1, C16.1, R5.1, R7.2, U2.6 (OUT)

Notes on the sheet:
3.0
00000007
Braingeneers
RasPi Header
SPI CABLE ADAPTER PINS
LVDS
Power
5V to 3.5V
5V to 3.3V
Test Points

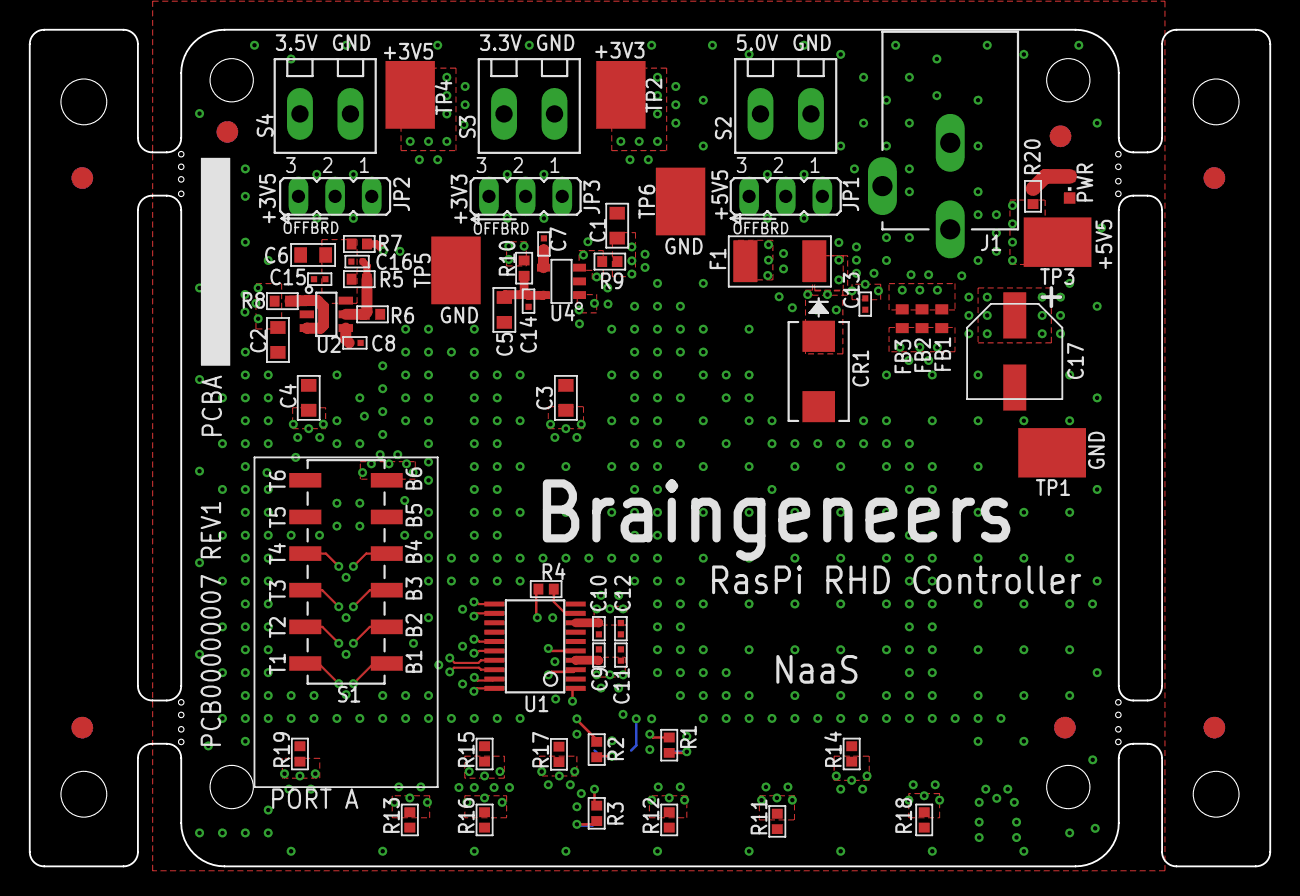
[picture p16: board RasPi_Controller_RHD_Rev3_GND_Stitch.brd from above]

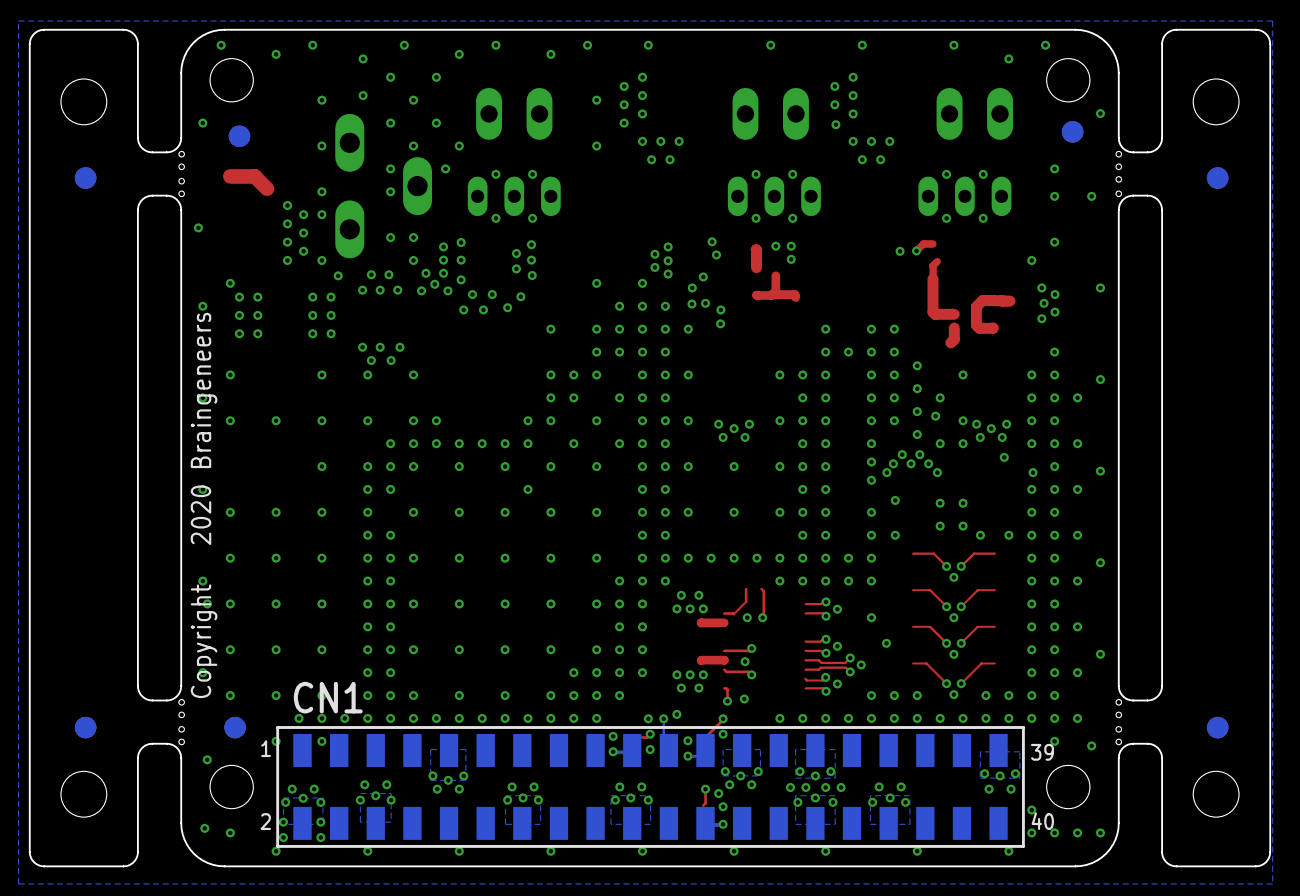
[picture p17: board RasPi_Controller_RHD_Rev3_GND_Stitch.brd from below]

Board: 4 copper layers, 86.0 x 58.0 mm, 83 parts (7 on the bottom side), 45 nets.

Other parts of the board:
DRILEGEND: DRILEGEND
U$1, U$32, U$34, U$35, U$36, U$48, U$49, U$50, U$51, U$67, U$68, U$69, U$73, U$75: FIDUCIAL_G15
U$7: NASS_LOGO_LG
U$31: ROHS_LG
U$33: LOGO_BRAINGENEERS_H_12MM
U$52: A5L-LOC
U$70: NO_TRASH_LG
U$72: STATIC_LG
U$84: COMPYRIGHT_MED

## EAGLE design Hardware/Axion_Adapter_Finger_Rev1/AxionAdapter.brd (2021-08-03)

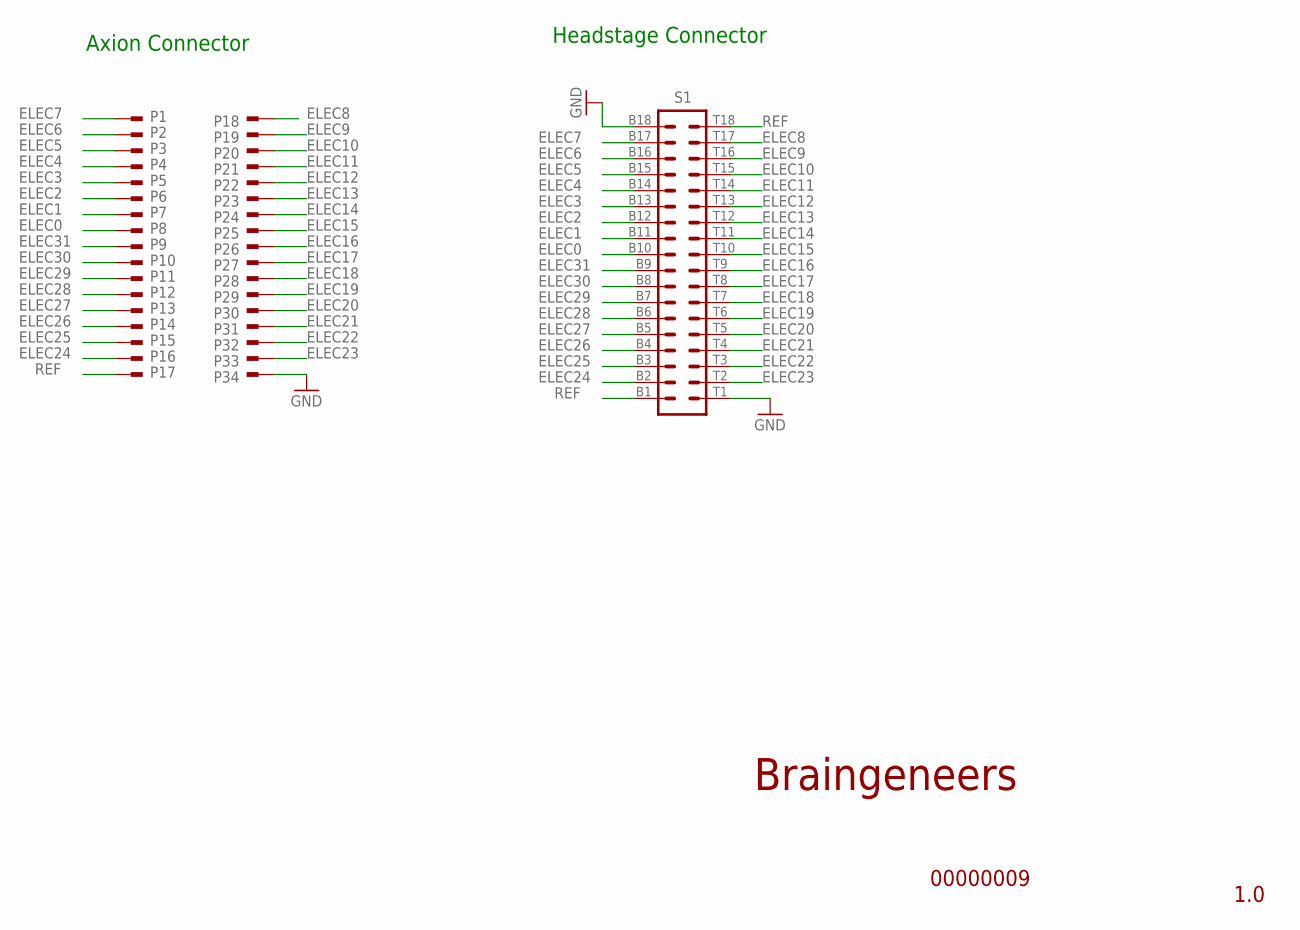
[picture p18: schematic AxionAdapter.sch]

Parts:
P1, P2, P3, P4, P5, P6, P7, P8, P9, P10, P11, P12, P13, P14, P15, P16, P17, P18, P19, P20, P21, P22, P23, P24, P25, P26, P27, P28, P29, P30, P31, P32, P33, P34: 2336713-2_TE
S1: OMNETICS_A79024

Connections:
ELEC0: P8.P$1, P8.P$2, S1.B10
ELEC1: P7.P$1, P7.P$2, S1.B11
ELEC2: P6.P$1, P6.P$2, S1.B12
ELEC3: P5.P$1, P5.P$2, S1.B13
ELEC4: P4.P$1, P4.P$2, S1.B14
ELEC5: P3.P$1, P3.P$2, S1.B15
ELEC6: P2.P$1, P2.P$2, S1.B16
ELEC7: P1.P$1, P1.P$2, S1.B17
ELEC8: P18.P$1, P18.P$2, S1.T17
ELEC9: P19.P$1, P19.P$2, S1.T16
ELEC10: P20.P$1, P20.P$2, S1.T15
ELEC11: P21.P$1, P21.P$2, S1.T14
ELEC12: P22.P$1, P22.P$2, S1.T13
ELEC13: P23.P$1, P23.P$2, S1.T12
ELEC14: P24.P$1, P24.P$2, S1.T11
ELEC15: P25.P$1, P25.P$2, S1.T10
ELEC16: P26.P$1, P26.P$2, S1.T9
ELEC17: P27.P$1, P27.P$2, S1.T8
ELEC18: P28.P$1, P28.P$2, S1.T7
ELEC19: P29.P$1, P29.P$2, S1.T6
ELEC20: P30.P$1, P30.P$2, S1.T5
ELEC21: P31.P$1, P31.P$2, S1.T4
ELEC22: P32.P$1, P32.P$2, S1.T3
ELEC23: P33.P$1, P33.P$2, S1.T2
ELEC24: P16.P$1, P16.P$2, S1.B2
ELEC25: P15.P$1, P15.P$2, S1.B3
ELEC26: P14.P$1, P14.P$2, S1.B4
ELEC27: P13.P$1, P13.P$2, S1.B5
ELEC28: P12.P$1, P12.P$2, S1.B6
ELEC29: P11.P$1, P11.P$2, S1.B7
ELEC30: P10.P$1, P10.P$2, S1.B8
ELEC31: P9.P$1, P9.P$2, S1.B9
GND: P34.P$1, P34.P$2, S1.B18, S1.T1
REF: P17.P$1, P17.P$2, S1.B1, S1.T18

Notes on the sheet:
1.0
00000009
Braingeneers
Headstage Connector
Axion Connector

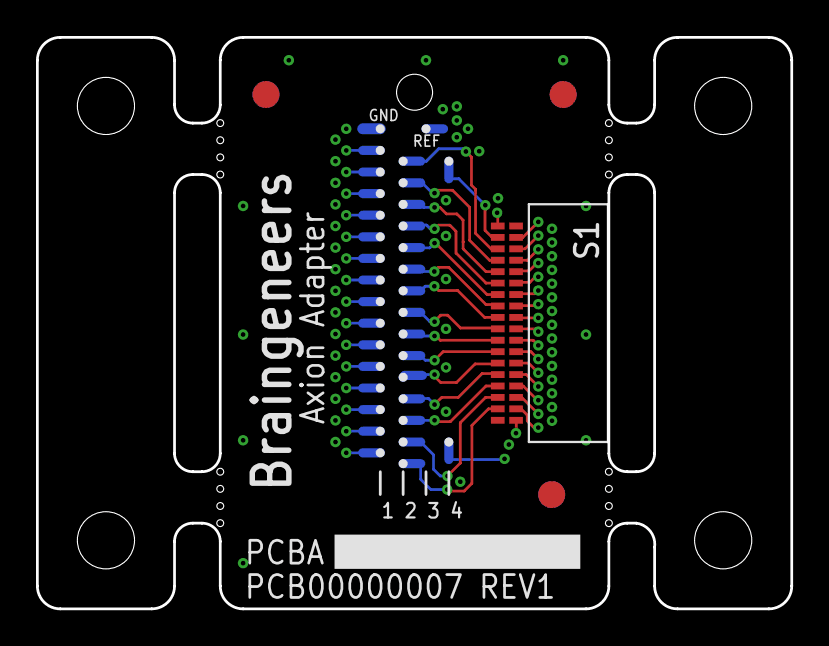
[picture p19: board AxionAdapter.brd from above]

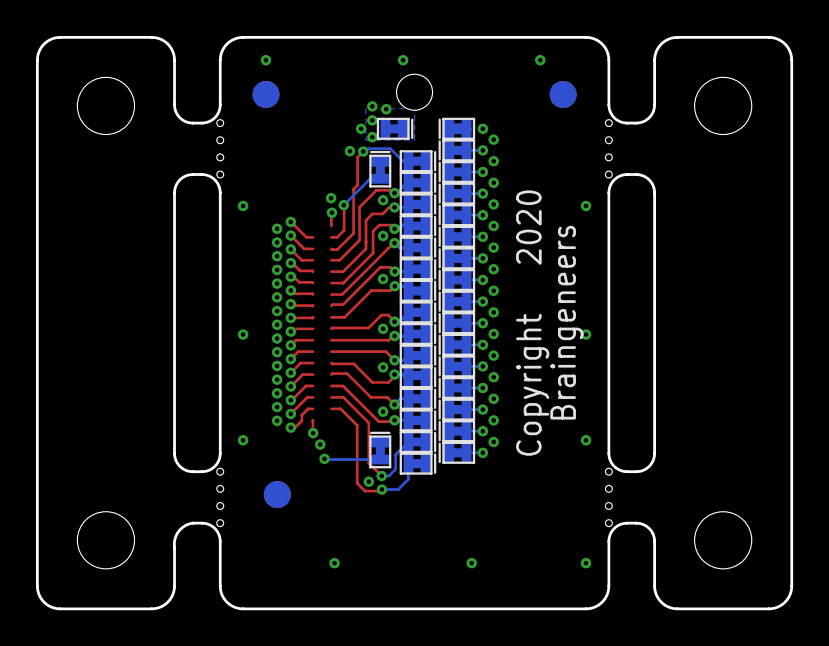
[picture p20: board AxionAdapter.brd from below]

Board: 4 copper layers, 41.9 x 31.8 mm, 48 parts (38 on the bottom side), 34 nets.

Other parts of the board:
DRILEGEND: DRILEGEND
U$1, U$2, U$35, U$49, U$50, U$73: FIDUCIAL_G15
U$7: NASS_LOGO_LG
U$31: ROHS_LG
U$52: A5L-LOC
U$70: NO_TRASH_LG
U$72: STATIC_LG
U$84: COMPYRIGHT_MED

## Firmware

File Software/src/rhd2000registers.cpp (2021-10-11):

//----------------------------------------------------------------------------------
// rhd2000registers.cpp
//
// Intan Technoloies RHD2000 Rhythm Interface API
// Rhd2000Registers Class
// Version 1.5.3 (26 August 2019)
//
// Copyright (c) 2013-2019 Intan Technologies LLC
//
// This software is provided 'as-is', without any express or implied warranty.
// In no event will the authors be held liable for any damages arising from the
// use of this software.
//
// Permission is granted to anyone to use this software for any applications that
// use Intan Technologies integrated circuits, and to alter it and redistribute it
// freely.
//
// See http://www.intantech.com for documentation and product information.
//----------------------------------------------------------------------------------

#include <iostream>
#include <iomanip>
#include <cmath>
#include <vector>
#include <queue>

#include "rhd2000registers.h"

using namespace std;

// This class creates and manages a data structure representing the internal RAM registers on
// a RHD2000 chip, and generates command lists to configure the chip and perform other functions.
// Changing the value of variables within an instance of this class does not directly affect a
// RHD2000 chip connected to the FPGA; rather, a command list must be generated from this class
// and then downloaded to the FPGA board using Rhd2000EvalBoard::uploadCommandList.

// Constructor.  Set RHD2000 register variables to default values.
Rhd2000Registers::Rhd2000Registers(double sampleRate)
{
    aPwr.resize(64);

    defineSampleRate(sampleRate);

    // Set default values for all register settings
    adcReferenceBw = 3;         // ADC reference generator bandwidth (0 [highest BW] - 3 [lowest BW]);
                                // always set to 3
    setFastSettle(false);       // amplifier fast settle (off = normal operation)
    ampVrefEnable = 1;          // enable amplifier voltage references (0 = power down; 1 = enable);
                                // 1 = normal operation
    adcComparatorBias = 3;      // ADC comparator preamp bias current (0 [lowest] - 3 [highest], only
                                // valid for comparator select = 2,3); always set to 3
    adcComparatorSelect = 2;    // ADC comparator select; always set to 2

    vddSenseEnable = 1;         // supply voltage sensor enable (0 = disable; 1 = enable)
    // adcBufferBias = 32;      // ADC reference buffer bias current (0 [highest current] - 63 [lowest current]);
                                // This value should be set according to ADC sampling rate; set in setSampleRate()

    // muxBias = 40;            // ADC input MUX bias current (0 [highest current] - 63 [lowest current]);
                                // This value should be set according to ADC sampling rate; set in setSampleRate()

    // muxLoad = 0;             // MUX capacitance load at ADC input (0 [min CL] - 7 [max CL]); LSB = 3 pF
                                // Set in setSampleRate()

    tempS1 = 0;                 // temperature sensor S1 (0-1); 0 = power saving mode when temperature sensor is
                                // not in use
    tempS2 = 0;                 // temperature sensor S2 (0-1); 0 = power saving mode when temperature sensor is
                                // not in use
    tempEn = 0;                 // temperature sensor enable (0 = disable; 1 = enable)
    setDigOutHiZ();             // auxiliary digital output state

    weakMiso = 1;               // weak MISO (0 = MISO line is HiZ when CS is inactive; 1 = MISO line is weakly
                                // driven when CS is inactive)
    twosComp = 1;               // two's complement ADC results (0 = unsigned offset representation; 1 = signed
                                // representation)
    absMode = 0;                // absolute value mode (0 = normal output; 1 = output passed through abs(x) function)
    enableDsp(true);            // DSP offset removal enable/disable
    setDspCutoffFreq(1.0);      // DSP offset removal HPF cutoff freqeuncy

    zcheckDacPower = 1;         // impedance testing DAC power-up (0 = power down; 1 = power up)
    zcheckLoad = 0;             // impedance testing dummy load (0 = normal operation; 1 = insert 60 pF to ground)
    setZcheckScale(ZcheckCs100fF);  // impedance testing scale factor (100 fF, 1.0 pF, or 10.0 pF)
    zcheckConnAll = 0;          // impedance testing connect all (0 = normal operation; 1 = connect all electrodes together)
    setZcheckPolarity(ZcheckPositiveInput); // impedance testing polarity select (RHD2216 only) (0 = test positive inputs;
                                // 1 = test negative inputs)
    enableZcheck(false);        // impedance testing enable/disable

    setZcheckChannel(0);        // impedance testing amplifier select (0-63)

    offChipRH1 = 0;             // bandwidth resistor RH1 on/off chip (0 = on chip; 1 = off chip)
    offChipRH2 = 0;             // bandwidth resistor RH2 on/off chip (0 = on chip; 1 = off chip)
    offChipRL = 0;              // bandwidth resistor RL on/off chip (0 = on chip; 1 = off chip)
    adcAux1En = 0;              // enable ADC aux1 input (when RH1 is on chip) (0 = disable; 1 = enable)
    adcAux2En = 0;              // enable ADC aux2 input (when RH2 is on chip) (0 = disable; 1 = enable)
    adcAux3En = 0;              // enable ADC aux3 input (when RL is on chip) (0 = disable; 1 = enable)

    setUpperBandwidth(10000.0); // set upper bandwidth of amplifiers
    setLowerBandwidth(1.0);     // set lower bandwidth of amplifiers

    powerUpAllAmps();           // turn on all amplifiers
}

// Define RHD2000 per-channel sampling rate so that certain sampling-rate-dependent registers are set correctly
// (This function does not change the sampling rate of the FPGA; for this, use Rhd2000EvalBoard::setSampleRate.)
void Rhd2000Registers::defineSampleRate(double newSampleRate)
{
    sampleRate = newSampleRate;

    muxLoad = 0;

    if (sampleRate < 3334.0) {     // S/s/ch
        muxBias = 40;
        adcBufferBias = 32;
    } else if (sampleRate < 4001.0) {
        muxBias = 40;
        adcBufferBias = 16;
    } else if (sampleRate < 5001.0) {
        muxBias = 40;
        adcBufferBias = 8;
    } else if (sampleRate < 6251.0) {
        muxBias = 32;
        adcBufferBias = 8;
    } else if (sampleRate < 8001.0) {
        muxBias = 26;
        adcBufferBias = 8;
    } else if (sampleRate < 10001.0) {
        muxBias = 18;
        adcBufferBias = 4;
    } else if (sampleRate < 12501.0) {
        muxBias = 16;
        adcBufferBias = 3;
    } else if (sampleRate < 15001.0) {
        muxBias = 7;
        adcBufferBias = 3;
    } else {
        muxBias = 4;
        adcBufferBias = 2;
    }
}

// Use the muxBias and adcBufferBias to determine sample rate per channel
int Rhd2000Registers::getSampleRate(int adcBuffer, int mux)
{
    int sampleRateChannel;
    if (mux == 40 && adcBuffer == 32) {
        sampleRateChannel = 3333;
    } else if (mux == 40 && adcBuffer == 16) {
        sampleRateChannel = 4000;
    } else if (mux == 40 && adcBuffer == 8) {
        sampleRateChannel = 5000;
    } else if (mux == 32 && adcBuffer == 8) {
        sampleRateChannel = 6250;
    } else if (mux == 26 && adcBuffer == 8) {
        sampleRateChannel = 8000;
    } else if (mux == 18 && adcBuffer == 4) {
        sampleRateChannel = 10000;
    } else if (mux == 16 && adcBuffer == 3) {
        sampleRateChannel = 12500;
    } else if (mux == 7 && adcBuffer == 3) {
        sampleRateChannel = 15000;
    } else if (mux == 4 && adcBuffer == 2) {
        sampleRateChannel = 20000;;
    } else {
        sampleRateChannel = 0;
    }
    
    return sampleRateChannel;
}

// Enable or disable amplifier fast settle function; drive amplifiers to baseline
// if enabled.
void Rhd2000Registers::setFastSettle(bool enabled)
{
    ampFastSettle = (enabled ? 1 : 0);
}

// Drive auxiliary digital output low
void Rhd2000Registers::setDigOutLow()
{
    digOut = 0;
    digOutHiZ = 0;
}

// Drive auxiliary digital output high
void Rhd2000Registers::setDigOutHigh()
{
    digOut = 1;
    digOutHiZ = 0;
}

// Set auxiliary digital output to high-impedance (HiZ) state
void Rhd2000Registers::setDigOutHiZ()
{
    digOut = 0;
    digOutHiZ = 1;
}

// Enable or disable ADC auxiliary input 1
void Rhd2000Registers::enableAux1(bool enabled)
{
    adcAux1En = (enabled ? 1 : 0);
}

// Enable or disable ADC auxiliary input 2
void Rhd2000Registers::enableAux2(bool enabled)
{
    adcAux2En = (enabled ? 1 : 0);
}

// Enable or disable ADC auxiliary input 3
void Rhd2000Registers::enableAux3(bool enabled)
{
    adcAux3En = (enabled ? 1 : 0);
}

// Enable or disable DSP offset removal filter
void Rhd2000Registers::enableDsp(bool enabled)
{
    dspEn = (enabled ? 1 : 0);
}

// Set the DSP offset removal filter cutoff frequency as closely to the requested
// newDspCutoffFreq (in Hz) as possible; returns the actual cutoff frequency (in Hz).
double Rhd2000Registers::setDspCutoffFreq(double newDspCutoffFreq)
{
    int n;
    double x, fCutoff[16], logNewDspCutoffFreq, logFCutoff[16], minLogDiff;
    const double Pi = 2*acos(0.0);

    fCutoff[0] = 0.0;   // We will not be using fCutoff[0], but we initialize it to be safe

    logNewDspCutoffFreq = log10(newDspCutoffFreq);

    // Generate table of all possible DSP cutoff frequencies
    for (n = 1; n < 16; ++n) {
        x = pow(2.0, (double) n);
        fCutoff[n] = sampleRate * log(x / (x - 1.0)) / (2*Pi);
        logFCutoff[n] = log10(fCutoff[n]);
        // cout << "  fCutoff[" << n << "] = " << fCutoff[n] << " Hz" << endl;
    }

    // Now find the closest value to the requested cutoff frequency (on a logarithmic scale)
    if (newDspCutoffFreq > fCutoff[1]) {
        dspCutoffFreq = 1;
    } else if (newDspCutoffFreq < fCutoff[15]) {
        dspCutoffFreq = 15;
    } else {
        minLogDiff = 10000000.0;
        for (n = 1; n < 16; ++n) {
            if (fabs(logNewDspCutoffFreq - logFCutoff[n]) < minLogDiff) {
                minLogDiff = fabs(logNewDspCutoffFreq - logFCutoff[n]);
                dspCutoffFreq = n;
            }
        }
    }

    return fCutoff[dspCutoffFreq];
}

// Returns the current value of the DSP offset removal cutoff frequency (in Hz).
double Rhd2000Registers::getDspCutoffFreq() const
{
    double x;
    const double Pi = 2*acos(0.0);

    x = pow(2.0, (double) dspCutoffFreq);

    return sampleRate * log(x / (x - 1.0)) / (2*Pi);
}

// Enable or disable impedance checking mode
void Rhd2000Registers::enableZcheck(bool enabled)
{
    zcheckEn = (enabled ? 1: 0);
}

// Power up or down impedance checking DAC
void Rhd2000Registers::setZcheckDacPower(bool enabled)
{
    zcheckDacPower = (enabled ? 1 : 0);
}

// Select the series capacitor used to convert the voltage waveform generated by the on-chip
// DAC into an AC current waveform that stimulates a selected electrode for impedance testing
// (ZcheckCs100fF, ZcheckCs1pF, or Zcheck10pF).
void Rhd2000Registers::setZcheckScale(ZcheckCs scale)
{
    switch (scale) {
        case ZcheckCs100fF:
            zcheckScale = 0x00;     // Cs = 0.1 pF
            break;
        case ZcheckCs1pF:
            zcheckScale = 0x01;     // Cs = 1.0 pF
            break;
        case ZcheckCs10pF:
            zcheckScale = 0x03;     // Cs = 10.0 pF
            break;
    }
}

// Select impedance testing of positive or negative amplifier inputs (RHD2216 only), based
// on the variable polarity (ZcheckPositiveInput or ZcheckNegativeInput)
void Rhd2000Registers::setZcheckPolarity(ZcheckPolarity polarity)
{
    switch (polarity) {
        case ZcheckPositiveInput:
            zcheckSelPol = 0;
            break;
    case ZcheckNegativeInput:
            zcheckSelPol = 1;
            break;
    }
}
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

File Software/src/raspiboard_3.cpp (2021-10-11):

//----------------------------------------------------------------------------------
// Rhd2000evalboard.cpp
//
// Intan Technoloies Rhd2000 Interface API
// Rhd2000EvalBoard Class
// Version 1.01 (28 March 2017)
//
// Copyright (c) 2013-2017 Intan Technologies LLC
//
// This software is provided 'as-is', without any express or implied warranty.
// In no event will the authors be held liable for any damages arising from the
// use of this software.
//
// Permission is granted to anyone to use this software for any applications that
// use Intan Technologies integrated circuits, and to alter it and redistribute it
// freely.
//
// See http://www.intantech.com for documentation and product information.
//----------------------------------------------------------------------------------

#include <iostream>
#include <unistd.h>
#include <iomanip>
#include <fstream>
#include <vector>
#include <queue>
#include <cmath>
#include <mutex>
#include <ctime>
#include <algorithm>
#include <bitset>
#include <thread>
#include <chrono>
#include <cstdlib>
#include <string>
#include <sw/redis++/redis++.h>
#include <jsoncpp/json/json.h>

#include "raspiboard.h"
extern "C" {
#include "bcm2835.h"
}

#include "rhd2000registers.h"


// Constructor
RaspiBoard::RaspiBoard(int commandLoop)
{
   // redisSec = 6;        // 6 seconds
   // fileRecTime = 2*60;  // 2 minutes, in seconds
   // dataQueue->maxTime = fileRecTime/redisSec;  // this number should always be an integer
   // cout << "Recording time for each dataset is: "<< fileRecTime/60 << " mins" << endl;
    // init board
    bcm2835_init();
    if (!bcm2835_init()) {
      cout << "bcm2835_init failed. Are you running as root??\n" << endl;     // for debug, delete later
    }
    bcm2835_spi_begin();
    if (!bcm2835_spi_begin()) {
      cout << "bcm2835_spi_begin failed. Are you running as root??\n" << endl;
    }
    else {
      cout << "Spi initiated" << endl;
        }
        
    bcm2835_spi_setBitOrder(BCM2835_SPI_BIT_ORDER_MSBFIRST);
    bcm2835_spi_setDataMode(BCM2835_SPI_MODE1);  // Different from Intan chip setting
    bcm2835_spi_chipSelect(BCM2835_SPI_CS0);
    bcm2835_spi_setChipSelectPolarity(BCM2835_SPI_CS0, LOW);
    
    dspEnabled = true;
    
    thread tiot(&AwsIot::iotReadJson, awsiot);
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

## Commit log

2021-05-09 Hardware designs added
    [BOM_RasPi_Controller_PCBA1.xls, RasPi_Controller_RHD_Rev3_GND_Stitch.brd, RasPi_Controller_RHD_Rev3_GND_Stitch.sch, copper_bottom_l4.gbr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]
2021-08-03 Added mechanical, hardware, and image files
    [AxionAdapter.brd, AxionAdapter.sch, AxionPlateHolder_CNC_ClampBottom_Plastic.step, AxionPlateHolder_CNC_ClampTop_Aluminum.step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]
2021-08-03 Added electrode mapping description
2023-05-25 Added pogo pin Axion adapter design
    [AxionAdapterPogo.brd, AxionAdapterPogo.sch, BOM_AxionAdapterPogo_Rev1_PCBA1.xls, copper_bottom_l4.gbr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]

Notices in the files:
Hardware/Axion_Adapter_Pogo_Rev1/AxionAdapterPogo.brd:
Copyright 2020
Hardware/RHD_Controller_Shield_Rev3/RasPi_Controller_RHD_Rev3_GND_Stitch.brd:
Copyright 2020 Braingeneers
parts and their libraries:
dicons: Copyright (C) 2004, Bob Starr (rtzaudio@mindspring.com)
